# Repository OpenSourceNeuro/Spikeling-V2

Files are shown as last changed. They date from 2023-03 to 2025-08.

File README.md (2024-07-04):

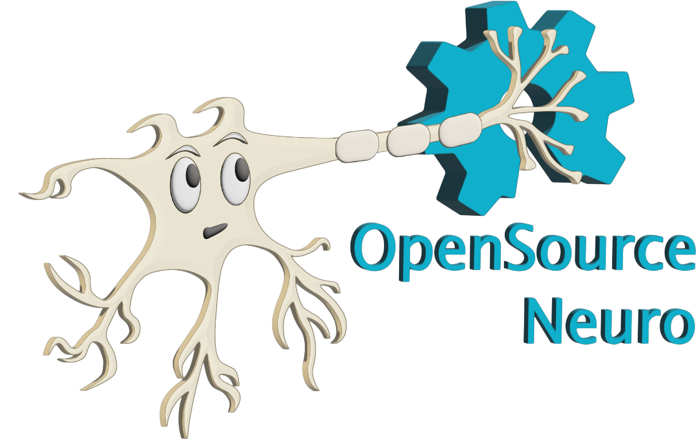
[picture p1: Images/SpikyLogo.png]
<p align="left">

<h1 align="center"> Spikeling V 2.2</h1></p>
<h3 align="center">  A hardware implementation of spiking neurons for neuroscience teaching and outreach</h3></p>
<p align="center"><h6 align="right">developed by M.J.Y. Zimmermann, A.M. Chagas & T. Baden</h6></p>

<br></br>



This project is licensed under the [GNU General Public License v3.0](https://github.com/OpenSourceNeuro/Spikeling-V2/blob/main/LICENSE)<br>
The hardware is licensed under the [CERN OHL v1.2](https://github.com/OpenSourceNeuro/Spikeling-V2/blob/main/PCB%20-%202.2c/LICENSE)

***

<p style='text-align: justify;'>
Understanding how neurons encode and compute information is fundamental to our study of the brain, but opportunities for hands-on experience with neurophysiological techniques on living neurons are scarce in science education.

<p style='text-align: justify;'>
Due to budgetary constraints and logistical hurdles, few students can be afforded the opportunity to experience electrophysiological recordings on living neurons in action. Yet, a fundamental aspect of neuroscience courses is to understand electrical signalling within neurons and the transmission of signals across synapses, as well as the experimental techniques necessary to observe these properties.

<p style='text-align: justify;'>
To support university-level neuroscience teaching, we designed ‘Spikeling’, an open-source teaching support device that mimics the electrical properties of spiking neurons by running the computationally efficient yet versatile Izhikevich model.

<p style='text-align: justify;'>
It is an artificial neuron that can receive different inputs, integrate them and outputs its computation, just like a spiking neuron would!

<p style='text-align: justify;'>
Technically, it consists on a microcontroller (an ESP32) running the computationally efficient Izhikevich model of a spiking neuron.

<br>

<div>
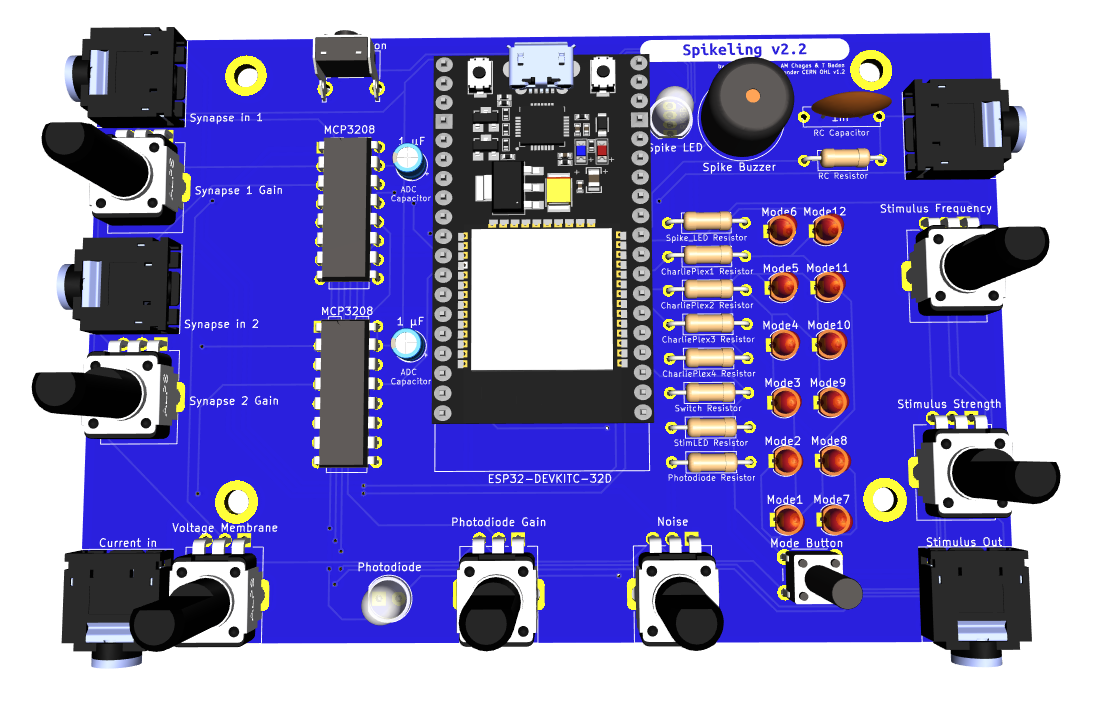
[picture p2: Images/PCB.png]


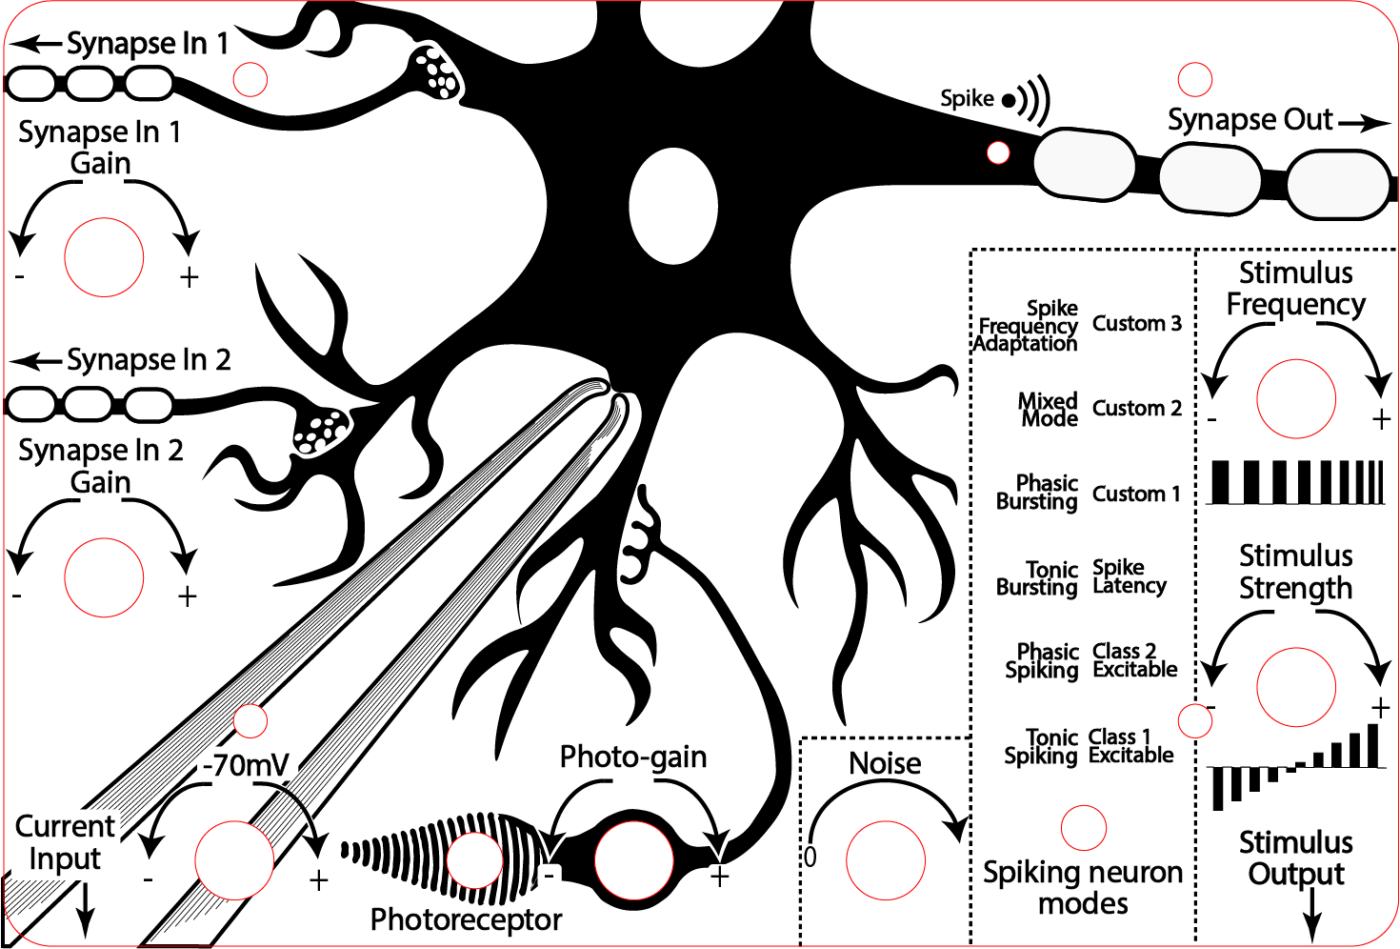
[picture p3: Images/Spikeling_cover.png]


<h6 align="center">Left: Rendering of spikeling electronic components. Right: Acrylic cover detailing spikeling functionalities.</h6>

</div>

<div>

<p style='text-align: justify;'>
The spikeling project emerged from local needs to teach neuroscience class modules for direct interaction with neuron physiology, data analysis, fluorescence imaging, protocol design, etc. The aim is to provide hands-on experience on how neurons encode information and how diverse variables modulates their activities, while engaging students with crucial aspects of data collection, experimental limitations, methodology and statistical analysis.

<p style='text-align: justify;'>
In order to give users a full interactive experience with the Spikeling neuron, a drawing engraved on the cover details in a neuro-morphic fashion all device functionalities. Furthermore, a spike-triggered LED and buzzer have been added to the device.

<p style='text-align: justify;'>
A dedicated GUI (Graphical User Interface) allows users to fully interact with Spikeling, plot all data generated and record them for further analysis.

<p style='text-align: justify;'>
Overall, Spikeling is a versatile device, allowing any teaching staff to conceive dry-lab tutorials or home assignments related to their own teaching course materials.

<p style='text-align: justify;'>
Enthusiasts and potential collaborators can source the electronic bits for this project from <a href="https://kitspace.org/boards/github.com/maxzimmer/spikeling-v2/">KitSpace</a></p>

</div>

***

<h2 align="center"> A brief summary of Spikeling functions</h3>

<br>

<div>

<h3 align="left"> Neurophysiology:</h3></p>

<p style='text-align: justify;'>
Spikeling is conceived on the Izhikevich model, which “reproduces spiking and bursting behaviour of known type of cortical neurons. The model combines the biologically plausibility of Hodgkin-Huxley-type dynamics and the computational efficiency of integrate-and-fire neurons” (E.M. Izhikevich, IEEE Transactions on Neural Networks, 2003, doi: 10.1109/TNN.2003.820440).

<p style='text-align: justify;'>
Students can appreciate playing with many variables that can be encountered in textbook or related to class material. A simulated patch-clamp experiment (represented by a pipette drawing on the top cover) allows students to “inject current” into the Spikeling neuron. They can furthermore modulate the amount of current injected, the speed and duration at which it is injected and observe the adaptation effect on a spiking neuron.

<p style='text-align: justify;'>
Spikeling also possesses a photodiode (modelized on the top cover as a photoreceptor) making Spikeling photo-sensitive. The photodiode mimics current inputs a photoreceptor would have on a spiking neuron. Students can appreciate the impact of a flash light onto the photoreceptor and investigate the different effects it may have. Ultimately, a supplied LED can be connected to the stimulus port and can then be controlled in frequency and intensity for controlled experiments. Advanced variable such as photoreceptor decay and recovery rate could also be investigated.

<p style='text-align: justify;'>
Each Spikeling unit possesses one “axonal” output and two “dendritic” inputs. Each dendritic input possesses a knob that can modulate the synaptic gain positively or negatively (mimicking excitatory and inhibitory synapses). In advanced stages, students could be encouraged to form neuronal networks. Auxiliary neurons can furthermore be stimulated synchronously from the “main neuron” experiment box to set a controlled environment.

</div>

<br>

<div>



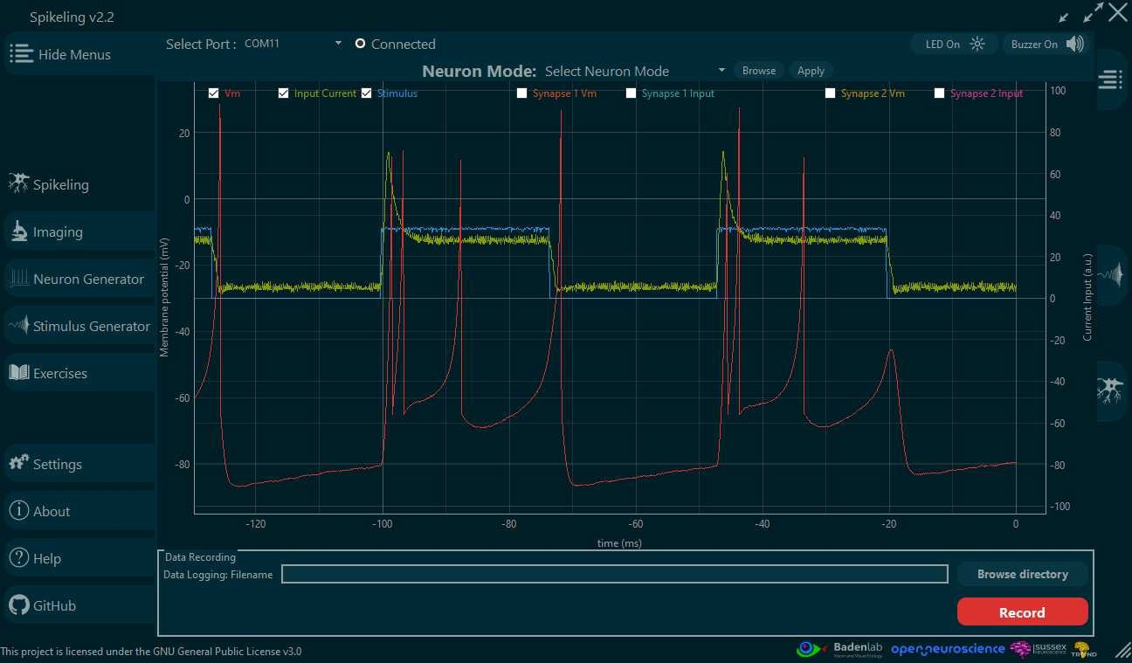
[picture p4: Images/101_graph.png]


<h6 align="center">Left: A Spikeling unit being stimulated by a direct current injection (blue cable) while receiving synaptic inputs from a second unit (pink cable). Right: Spikeling GUI displaying the unit membrane voltage (red trace) while being light-stimulated by a controlled LED (blue trace) which generates input current (green trace).</h6>

</div>

<br>

***

<br>

<div>

<h3 align="left"> Data analysis</h3></p>

<p style='text-align: justify;'>
Handling large dataset is an important part of daily academic work. However, few universities offer coding and programming modules for their neuroscience courses. A proper data analysis of any kind starts with the understanding of a program language and the understanding of every steps of the analysis pipeline. Only then, students can appreciate the results of their experiments and engage in their critical interpretation.

<p style='text-align: justify;'>
Any data generated by Spikeling can be saved and exported.  The GUI comes with a simple built-in data analysis that allows students to check their data and generate raster plots. From this simple analysis they could appreciate how neuronal information is encoded within stochastic spike trains (see below).

<p style='text-align: justify;'>
This simple analysis could be used for home assignments in the early stages of student degree before engaging them in developing their own analysis code.

<p style='text-align: justify;'>
For advanced data analysis and basic statistics, python notebooks are provided to serve as template for the teaching staff. It is our hope to create a Spikeling community where users could share courses, exercises and data analysis scripts to be widely used in neuroscience and coding courses.

</div>

<br>

<div>

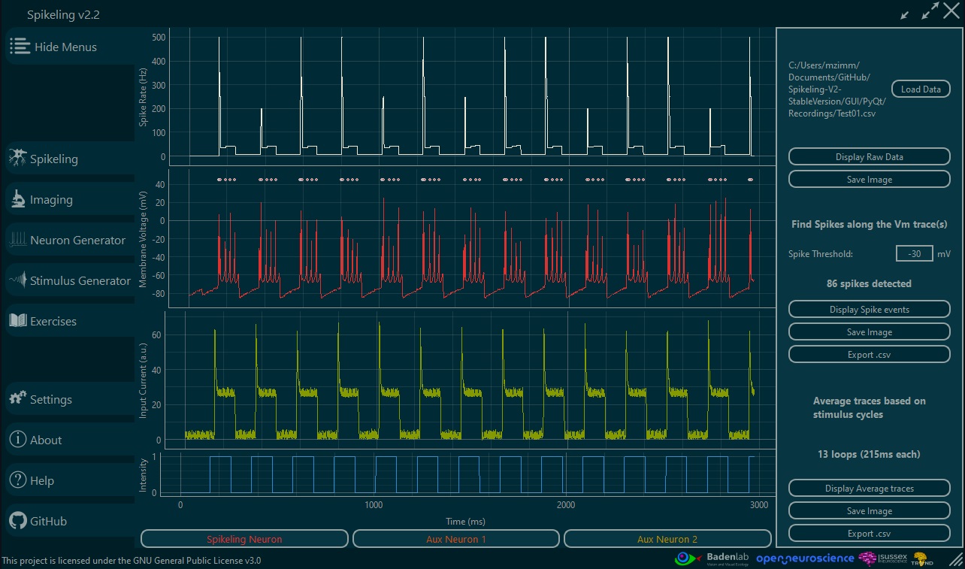
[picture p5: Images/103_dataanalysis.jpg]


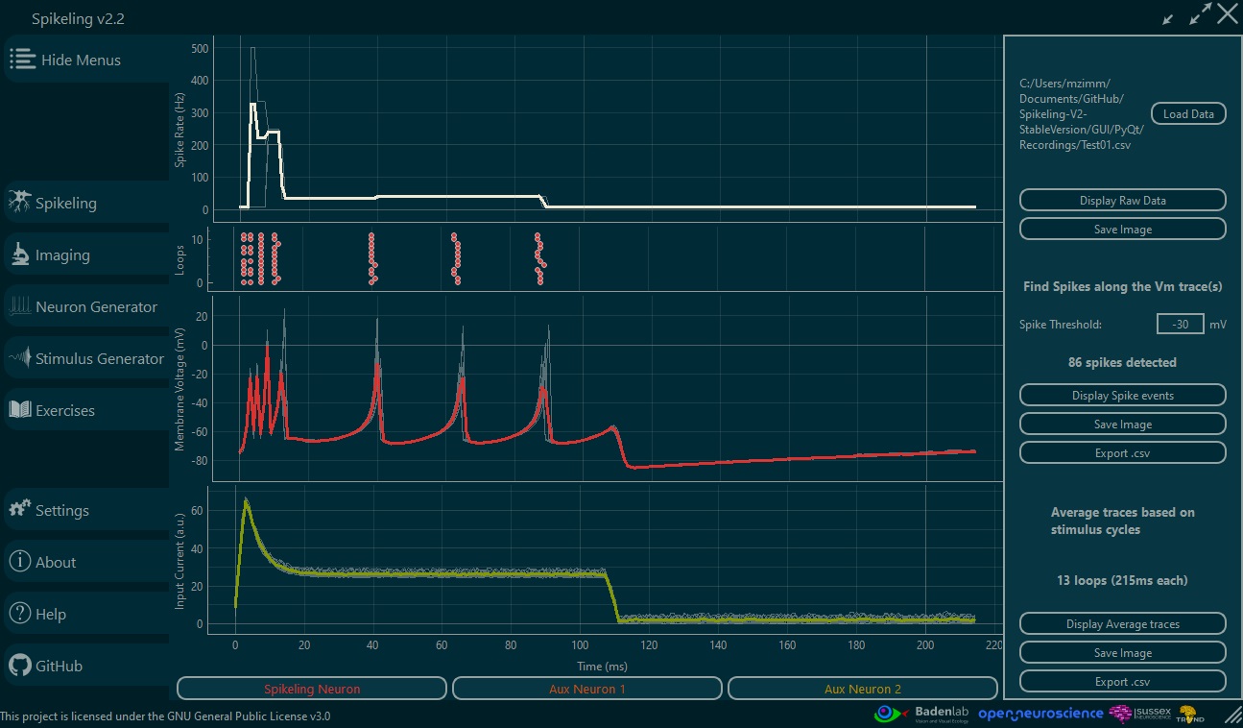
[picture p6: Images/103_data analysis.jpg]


<h6 align="center">GUI displaying the “Neuron Generator” page where users can appreciate the model underlying Spikeling activity and from which they can generate unique neuron to further run on Spikeling.</h6>

</div>

<br>

***

<br>

<div>

<h3 align="left">Stimulus generator:</h3>

<p style='text-align: justify;'>
Spikeling comes by default with a repeated square wave pattern stimulus, on which the user could only modulate the intensity and the frequency, might it be for direct current injection or light stimulation.

<p style='text-align: justify;'>
Here users are encouraged to develop their own stimulus (successive waves, sinusoidal loops, chirp, binary noise, etc.). Some basic stimuli are already available. The main point of this feature is to encourage the students to conceive their own experiments leading them to think about the protocol that needs to be implemented in order to answer the experimental questions they are being faced with.

</div>

<br>

<div>

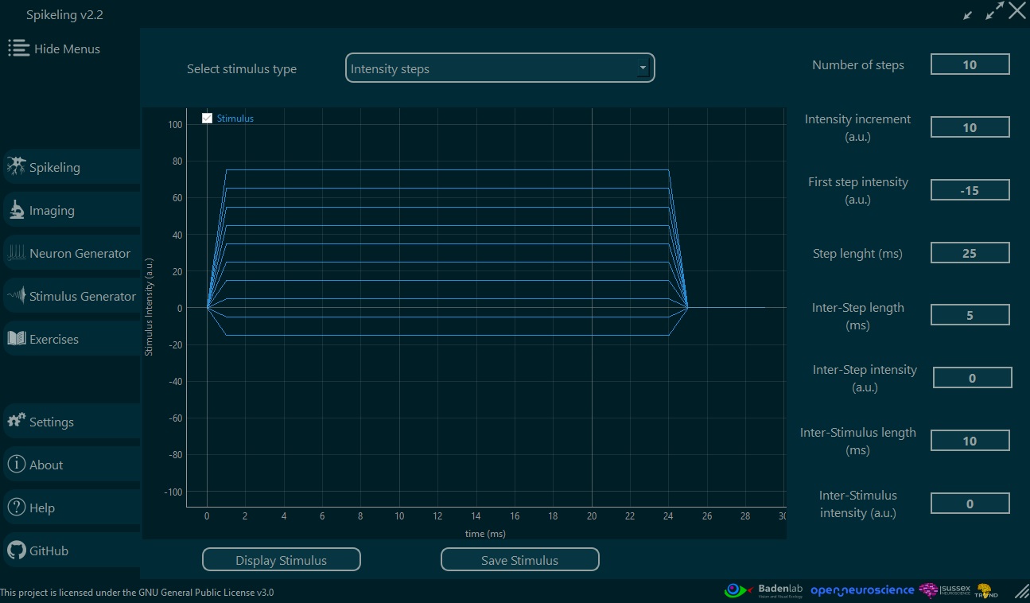
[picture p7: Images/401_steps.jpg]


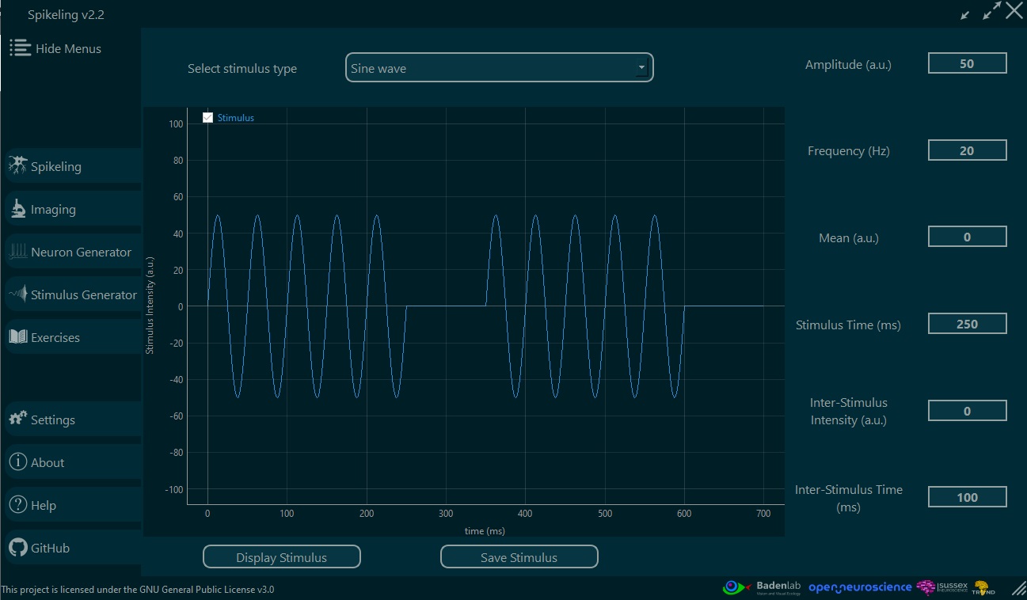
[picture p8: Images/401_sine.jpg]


<h6 align="center">GUI displaying the “Simulus Generator” page where users can generate their own unique stimuli. The left screen shows repetitive increments of current, as seen in classic electrophysiology experiments (10 steps with 10 a.u. current increment lasting 25 ms with a resting period of 5ms at 0 a.u. current). The right screen shows a sine wave stimulus (50 a.u. amplitude, 20 Hz frequency over a period of 250 ms and a resting period of 100 ms at 0 a.u. current)</h6>

</div>

<br>

***

<br>

<div>

<h3 align="left">Fluorescence imaging simulation:</h3>

<p style='text-align: justify;'>
Since Spikeling generates membrane voltage data, we could use this “ground truth data” to generate a simulated calcium concentration transient underlying spike occurrence in the neuron. And from then, use the later to model a simulated fluorescence.

<p style='text-align: justify;'>
Students could then be engaged into dynamic calcium fluorescence imaging (i.e two-photon microscopy) and play with many variables that could be encountered from the experimenter side (frame rate, laser power, photo detector gain, etc.), from the calcium concentration properties within the neuron (concentration baseline, decay, increase jump per spike, etc.)  or from the calcium indicator properties itself (indicator affinity, dissociation constant, brightness, photo-bleach, etc.).

<p style='text-align: justify;'>
For an even more realistic simulation, students could choose to move from a linear model to a non-linear saturation model of the fluorescence signal.

</div>

<br>

<div>

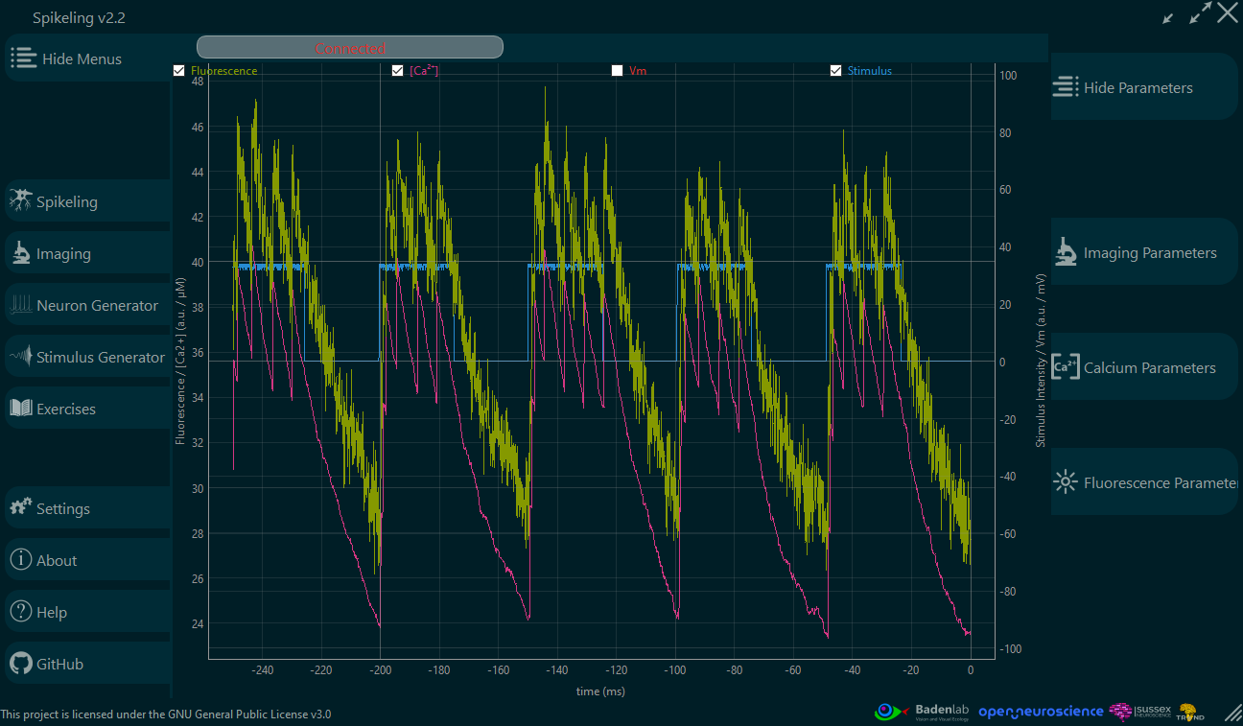
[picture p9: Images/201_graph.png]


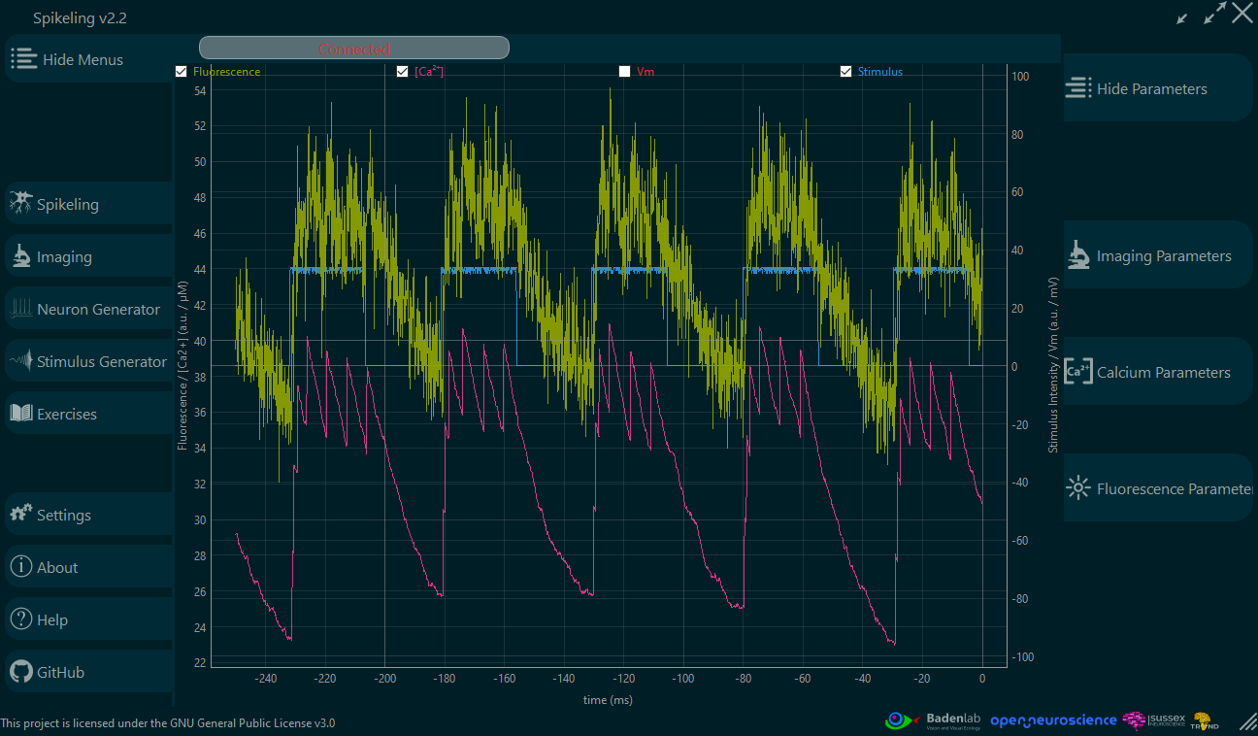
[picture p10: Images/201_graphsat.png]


<h6 align="center">GUI displaying linear(left) and (non-linear) models of simulated fluorescence (green) based on simulated calcium concentration (pink)</h6>

</div>

<div>

<p style='text-align: justify;'>
Here, the aim is to familiarise students with the type of data they could encounter in their future academic work, incorporating noise and limitations to the data that are inherent to every experiments.

<p style='text-align: justify;'>
Ultimately, students could be encouraged to analyse imaging data, even implement spike inference algorithms and compare their results to the “ground truth data” that generated the fluorescence trace.

</div>

<br>

***

<br>

<div>

<h3 align="left">Exercises:</h3>

<p style='text-align: justify;'>
Spikeling comes with a set of suggested exercises that could be used in class as a guideline for the teaching staff to explore Spikeling functionalities. They are conceived to allow students to make a concrete connection between neurophysiology concepts seen in lectures with a responsive in silico model.

<p style='text-align: justify;'>
Exercises are also a mean to introduce some epistemology into the teaching material: Understanding how a neurobiology concept became a knowledge and how it can be tested, confirmed or refuted.
In advance courses, giving students the opportunity to design their own experiment as assignment also allows to introduce good methodology and protocol design practices. Which, unfortunately has shown to be too often mistaken with methods.

<p style='text-align: justify;'>
We would always encourage teachers to develop their own exercises based on the content they cover in class. It is our hope that such exercises could also be used as homework grading system.

</div>

<br>

***

<br>

<h2 align="center">Detailed Spikeling functions</h3></p>

<br>

- [Spikeling: A spiking neuron interface](#a-spiking-neuron-interface)
- [Spikeling: GUI - neuron parameters](#spikeling-gui-neuron-parameters)
- [Spikeling: GUI - stimuli parameters](#spikeling-gui-stimuli-parameters)
- [Spikeling: Data Analysis](#-data-analysis)
- [Spikeling: Neuron generator](#spikeling-neuron-generator)
- [Spikeling: Stimulus Generator](#stimulus-generator)
- [Spikeling: Multiple recording](#spikeling-multiple-recording)

<br>

- [Fluorescence: imaging simulation](#fluorescence-imaging-simulation)
- [Fluorescence: Imaging parameters](#fluorescence-imaging-parameters)
- [Fluorescence: Calcium parameters](#fluorescence-calcium-parameters)
- [Fluorescence: Fluorescence parameters](#fluorescence-imaging-parameters)
- [Fluorescence: Data Analysis](#fluorescence-data-analysis)
- [Fluorescence: Multiple fluorescence](#fluorescence-multiple-fluorescence)

<br>

- [Exercices: GUI](#exercises-gui)
- [Exercices: Python](#exercises-python)

<br>

- [GitHub Contributions](#gitHub-Contributions)

- [Arduino code and libraries](#)

- [GUI PyQt6 / PySide6 script](#)

<br>

***

<br>

## A spiking neuron interface

<br>



<p style='text-align: justify;'>
The entire layout of the Spikeling board has been reconceived and a laser-cut acrylic sheet repesenting a neuron now sits on top of the board. All ports and potentiometers are now strategically placed.

<p style='text-align: justify;'>
The ESP32 is placed below the soma, the synaptic inputs from other Spikeling units are placed on the left, the synaptic output is placed on the right. Along the axon now sits a RGB LED, the red LED brightness follows as before the Vm status of the neuron, and the LED sparks in white when the neuron spike. The spike buzzer also sit along the axon, a small hole on the acrylic sheet sitting just above so the click can be heard coming from that direction. Both indicators can now be disabled by users at their pleasure.

<p style='text-align: justify;'>
The Vm potentiometer and the Current-in port are now grouped together and sit on the acrylic sheet at the bottom of an electrode pipette. They can now be considered as patch clamp experiment variables.

<p style='text-align: justify;'>
A photoreceptor is now drawn on the acrylic sheet, below the opsin sits a photodiode, and a potentiometer on the photoreceptor body now controls the photoreceptor sensitivity and its polarity (users can thus decide if the photoreceptor has an excitatory or an inhibitory effect on the neuron)

<p style='text-align: justify;'>
The noise potentiometer now sits in a box by itself as it represents parasitic noise from the experiment environment (synaptic inputs, receptor noise, thermal noise, experimental setup, etc.) and is independent from the rest of the Spikeling functions. This potentiometer is different from the others: it is not center-detented as it generates noise from a zero to a maximum value.

<p style='text-align: justify;'>
Next is the Neuron mode box which contains the twelve available modes to the users and a push button that allows the user to switch between them.

<p style='text-align: justify;'>
Finally, the last box contains all experimental tools allowing stimuli generation. As detailed on the acrylic top cover, the user can control the stimulus frequency and the stimulus intensity, along with its polarity. The stimulus output can either be directly connected to the current-in port to simulate a current applied to a patched neuron through the pipette; or be connected to a cable with a 5mm LED soldered at its tip which can be placed directly on top of the photoreceptor opsin (photodiode below). The photoreceptor potentiometer allows to modulate the gain and polarity of the light-induced input current. Furthermore, the photoreceptor possesses functions (on the GUI: decay/recovery) simulating how a variety of photoreceptors would integrate a light stimuli and how it will adapt to prolonged stimulation.  

<br>

***

<br>

<p style='text-align: justify;'>
Spikeling now possesses its own GUI, written in python and using the latest PyQt6/PySide6 library. The script then uses pyInstaller so it can be translated into a windows/linux/mac app, ready to be easily distributed to users.

<br>



<p style='text-align: justify;'>
The GUI is divided into distinct pages. The first one is the main GUI window where users connect the board to the computer. From there they can choose to either select the neuronal mode on the board directly (neuron mode box) or through the GUI (note that custom modes will have to be selected from here, and in this instance the GUI takes priority over the board commands).

<p style='text-align: justify;'>
The main window displays the Spikeling activity (Neuron Vm, total current input from all sources & stimulus ). If connected to other Spikelings, the GUI can display synaptic inputs: their incoming neuron Vm and their spiking events, which will be translated into input current for the main neuron. Traces can be selected through checkbox and superimposed over the same graph with a common timeline.

<p style='text-align: justify;'>
The "Neuron Mode" defines the current Izhikevich model being used [see Neuron Generator](#Spikeling-Neuron-generator). Twelve are encoded by default on the Spikeling unit and can be chosen either from the board itself or directly from the GUI: "Select Neuron Mode". Note that any command from the GUI will take priority over the board. Custom Neuron Modes can be selected from here and upload to the board.

<p style='text-align: justify;'>
The neuron interface page also possesses two buttons to enable/disable the spike buzzer sound and the spike LED, which in a class room full of spikeling, are regarded as huge relieves.

<p style='text-align: justify;'>
Below the main window, sits the recording window. All last generated data from traces that are checked on the main window will be saved in a .csv format.

<p style='text-align: justify;'>
On the right hand side two control columns can be found. For all commands, when the toggle button is enabled, the GUI takes over the potentiometer and controls directly the Spikeling variables. This allows users to design an experimental protocol in a controlled fashion.

<br>

***

<br>

<p style='text-align: justify;'>
Spikeling membrane voltage (Vm), displayed on the GUI in red, is generated by the Izhikevich model equation.
It is rather simple and relies on four parameters [see Neuron Generator](#Spikeling-Neuron-generator).

<br>

<p style='text-align: justify;'>
When Vm > 30mV, then a spike is generated, both the spike LED and spike buzzer on the board are activated, and the Vm model is reset accordingly (see above).

<p style='text-align: justify;'>
The green trace represents all current inputs received by the board and summed up in the variable "I" in the Izhikevich equation.
These current inputs correspond to the synaptic inputs, the direct current injection from the patch clamp port or the light induced current from the photodiode, and the noise generator potentiometer. All will influence the Vm equation and the subsequent spiking pattern.

<p style='text-align: justify;'>
The blue trace represents the square wave stimulus, which can be manually modulated in length, intensity and polarity through the potentiometer located in the "experiment box". The resulting stimulus signal is sent to the "Stimulus Output" port.
A jack cable connecting the "Stimulus Output" port to the "Current In" port will deliver the stimulus signal directly into the Spikeling neuron, simulating a direct current injection through a patched clamp electrode.
If a LED is connected to the "Stimulus Output" port and placed onto the photodiode, then the "photoreceptor" is stimulated accordingly and generates a current that will in turn be injected into the Izhikevich equation.

<p style='text-align: justify;'>
Users can also interact with the "Current In" potentiometer placed on the electrode and constantly inject steady current in order to either hyperpolarise or depolarise Spikeling.
Users can also interact with the "Photo-Gain" potentiometer and modulate the light sensitivity and polarity of the photodiode, thus generating ON/OFF neurons.

<p style='text-align: justify;'>
If Spikeling is connected to other units, the main window can display their Vm and their synaptic current inputs. Users can modulate these inputs by interacting with the "Synapse Gain" potentiometers which modulate the intensity and polarity of the synaptic inputs, giving rise to excitatory and inhibitory synapses.

<p style='text-align: justify;'>
Furthermore, users can stimulate the auxiliary Spikeling units in synchrony via the main unit's "Stimulus Output" port by using a splitter audio jack

<br>

***

<br>

## Spikeling GUI neuron parameters

<br>

TBC

<br>

***

<br>

## Spikeling GUI stimuli parameters

<br>

TBC

<br>

***

<br>

## Spikeling Neuron generator

<br>

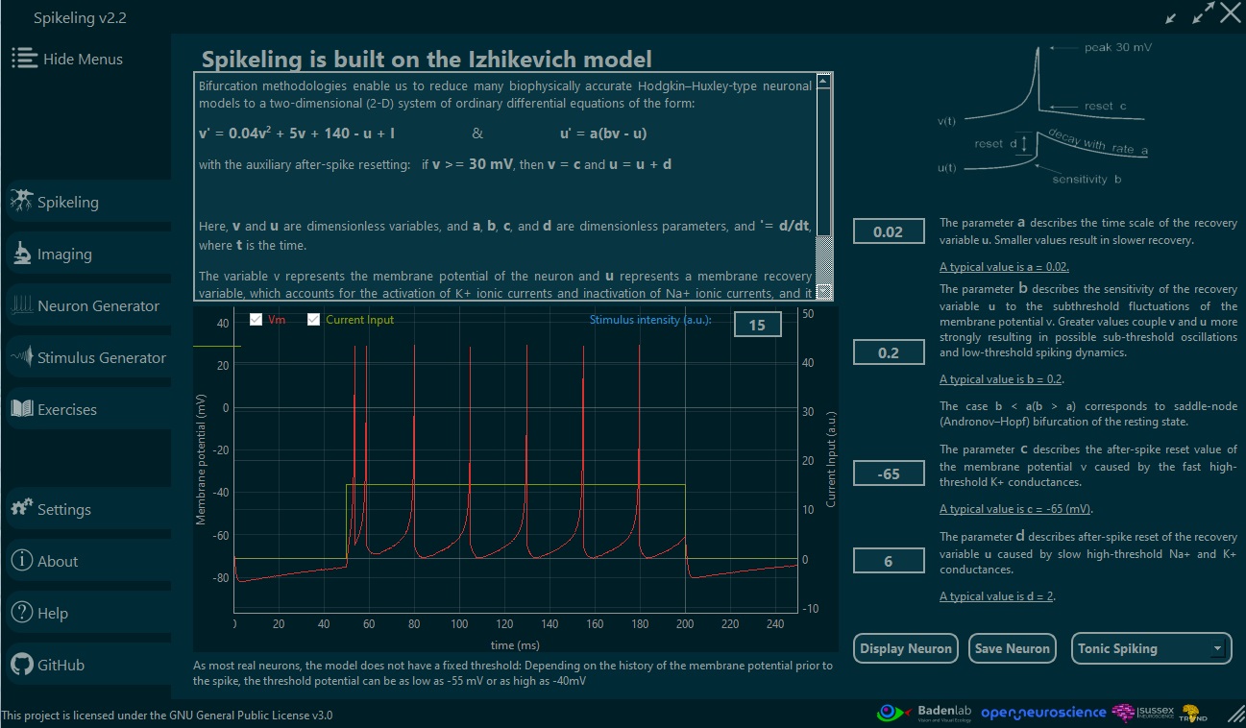
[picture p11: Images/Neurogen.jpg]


<p style='text-align: justify;'>
Spikeling GUI comes with a "Neuron Generator" page where users can interact with the Izhikevich equation, understand the model generating Spikeling membrane voltage, and create their own "neuron mode" to be loaded on the main page.

<p style='text-align: justify;'>
The main window computes the Izhikevich model with a modifiable current input. Users can change the 4 variable of the code and display the resulting "neuron mode". This is also where users can come up with their own neuronal modes to experiment on. This is also where teachers can generate their own custo-made neuron, save them, and impose them as experimental model for, i.e. home assignments.

<p style='text-align: justify;'>
From <a href="https://pubmed.ncbi.nlm.nih.gov/18244602">Izhikevich publication</a>:
<em> Bifurcation methodologies enable us to reduce many biophysically accurate Hodgkin–Huxley-type neuronal models to a two-dimensional (2-D) system of ordinary differential equations of the form:</em>

```math
v' = 0.04v^2 + 5v + 140 - u + I
```
```math
u' = a * (bv - u)
```

With the auxiliary after-spike resetting:

<p align="center">
if:
</p>

```math
v >= 30mV
```
<p align="center">
 then:
 </p>

 ```math
 v = c
 ```

<p align="center">
 and:
 </p>

 ```math
 u = u + d
```

<br>

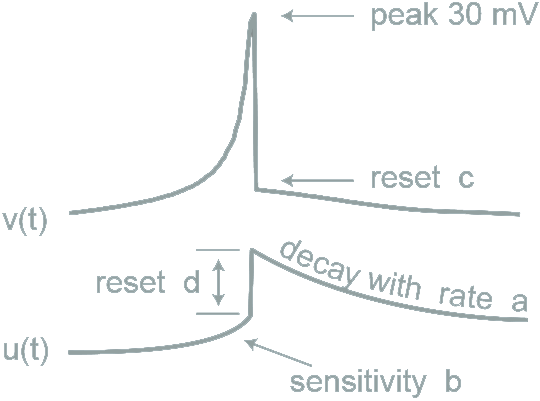
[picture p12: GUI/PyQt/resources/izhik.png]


<p style='text-align: justify;'>
Here, v and u are dimensionless variables, and a, b, c, and d are dimensionless parameters, and '= d/dt, where t is the time (0.1 µs).

<p style='text-align: justify;'>
The variable v represents the membrane potential of the neuron and u represents a membrane recovery variable, which accounts for the activation of K+ ionic currents and inactivation of Na+ ionic currents, and it provides negative feedback to v.

<p style='text-align: justify;'>
After the spike reaches its apex (+30 mV), the membrane voltage and the recovery variable are reset.
Synaptic currents or injected DC-currents are delivered via the variable I.

<p style='text-align: justify;'>
Below the stimulus frequency and strength sliders can be found a custom stimulus display. Here the user can choose to use instead of the classical square wave, either a stimulus from a pre-design library (comprising sine wave, chirp, white noise, etc.), or either a custom made stimulus generated from the GUI "stimulus generator" tab.

<br>

***

<br>

## Spikeling Stimulus Generator

<br>

<p style='text-align: justify;'>
Spikeling GUI also comes with a "Stimulus Generator" page where users can generate their own stimuli. In the current version seven distinct stimulus pattern are available with various parameters to interact with.
All stimuli can then be saved and further loaded from the Spikeling main window.

<br>

<div>





<h6 align="center">GUI displaying the “Simulus Generator” page where users can generate their own unique stimuli. The left screen shows repetitive increments of current, as seen in classic electrophysiology experiments (10 steps with 10 a.u. current increment lasting 25 ms with a resting period of 5ms at 0 a.u. current). The right screen shows a sine wave stimulus (50 a.u. amplitude, 20 Hz frequency over a period of 250 ms and a resting period of 100 ms at 0 a.u. current)</h6>

</div>

<br>

<div>

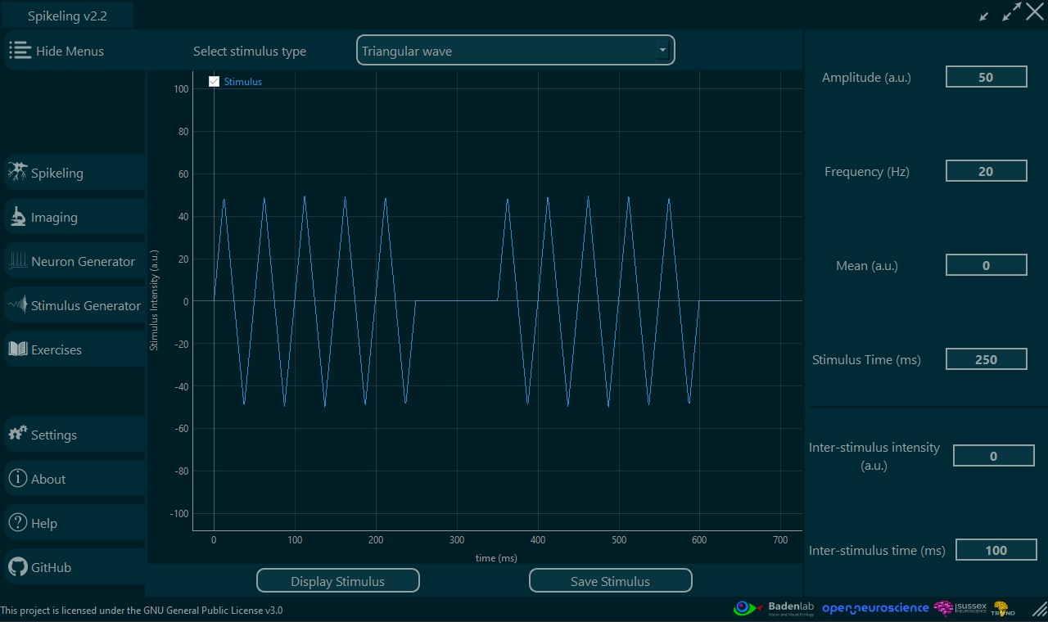
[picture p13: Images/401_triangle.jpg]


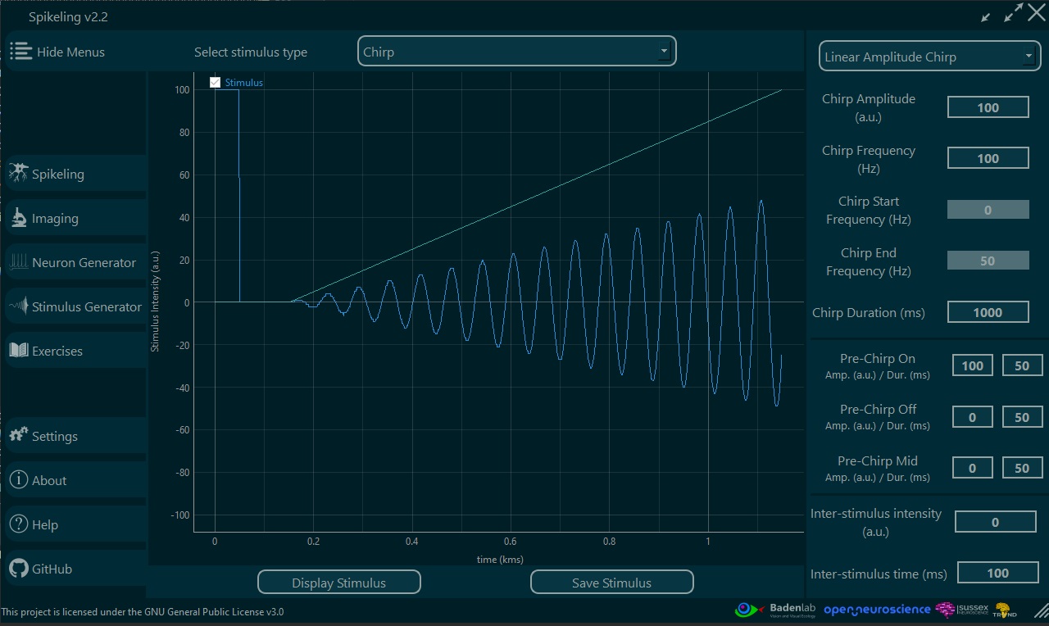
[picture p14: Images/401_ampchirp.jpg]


<h6 align="center">GUI displaying the “Simulus Generator” page where users can generate their own unique stimuli. The left screen shows a triangular wave stimulus (50 a.u. amplitude, 20 Hz frequency over a period of 250 ms and a resting period of 100 ms at 0 a.u. current). The right screen shows a chirp stimulus with an increased intensity from a 0 to a 100 a.u. amplitude at 100 Hz over 1000 ms </h6>

</div>

<br>

<div>

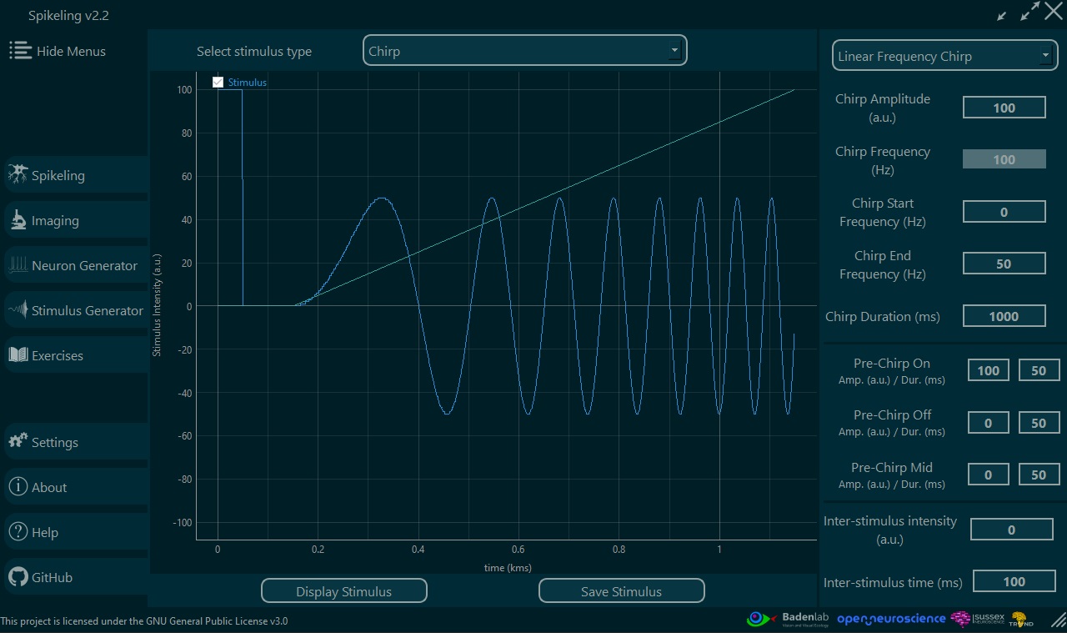
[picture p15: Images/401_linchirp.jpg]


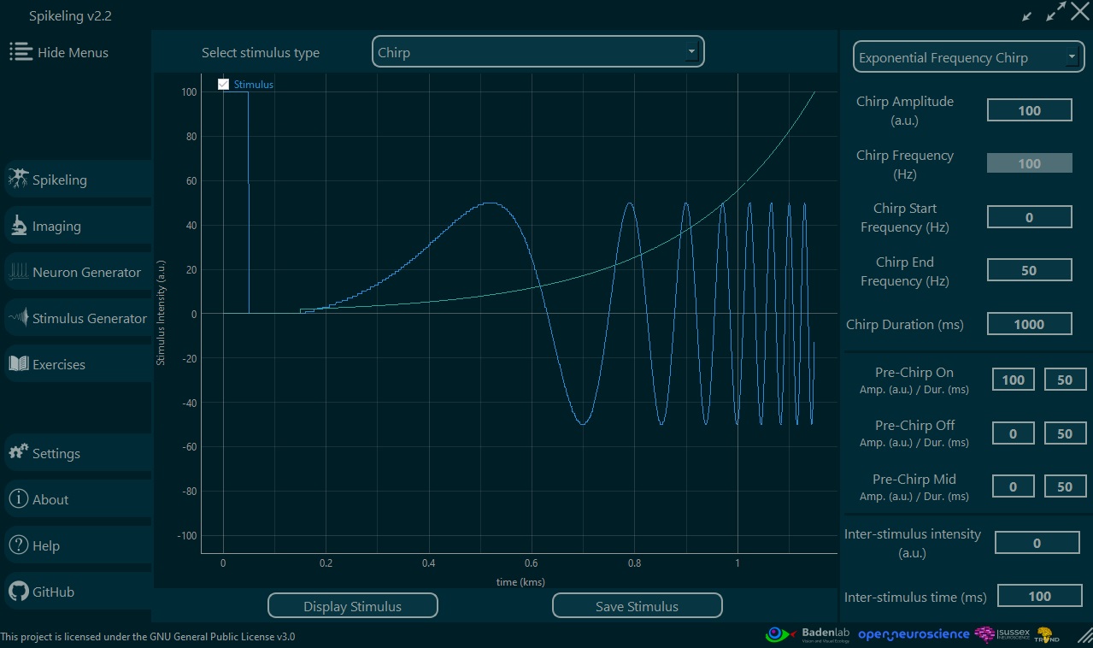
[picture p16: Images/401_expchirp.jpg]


<h6 align="center">GUI displaying the “Simulus Generator” page where users can generate their own unique stimuli. The left screen shows a linear chirp stimulus with an increased frequency from a 0 to a 50 Hz with an amplitude of 100 a.u. over 1000 ms. The right screen show the same stimulus with an exponential frequency increase </h6>

</div>

<br>

***

<br>

## Spikeling Multiple recording

<br>

TBC

<div>

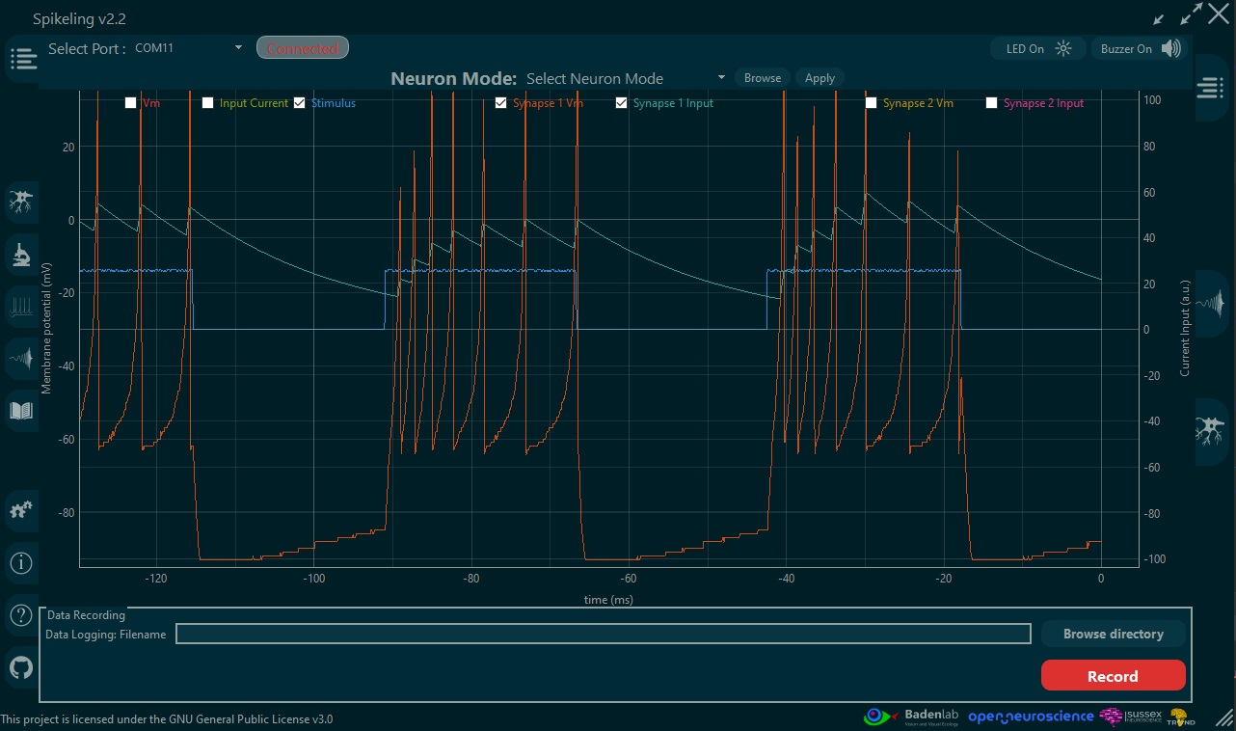
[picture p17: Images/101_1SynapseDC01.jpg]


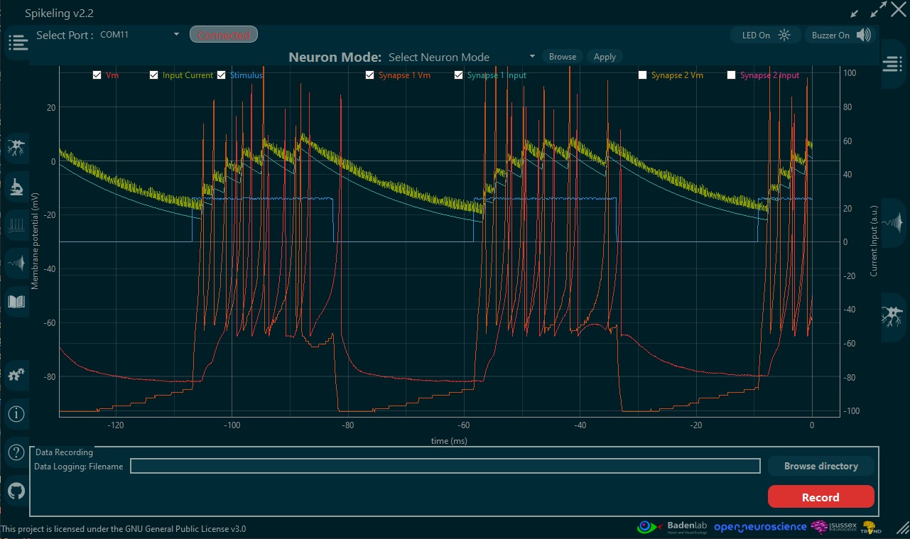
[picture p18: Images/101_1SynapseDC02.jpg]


<h6 align="center"> ... </h6>

</div>

<br>

<div>

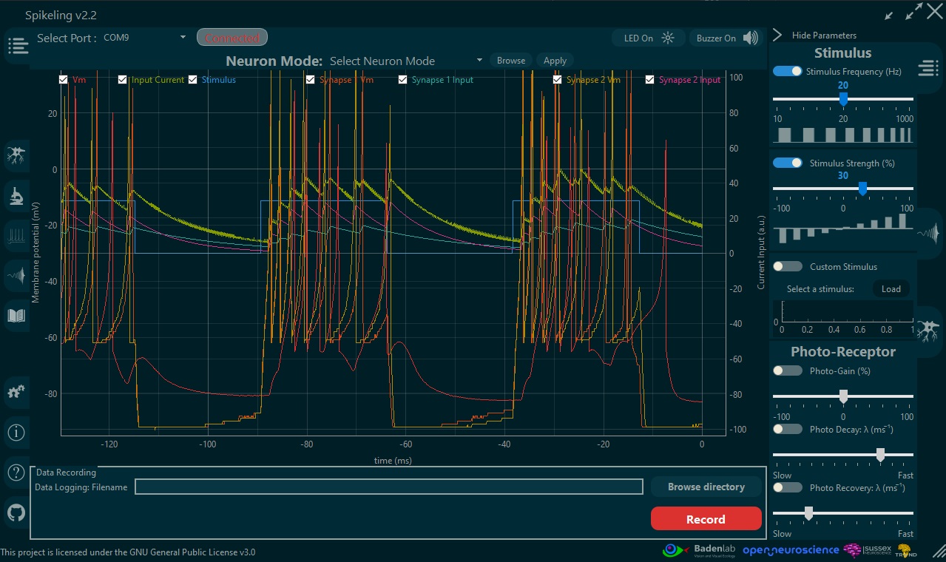
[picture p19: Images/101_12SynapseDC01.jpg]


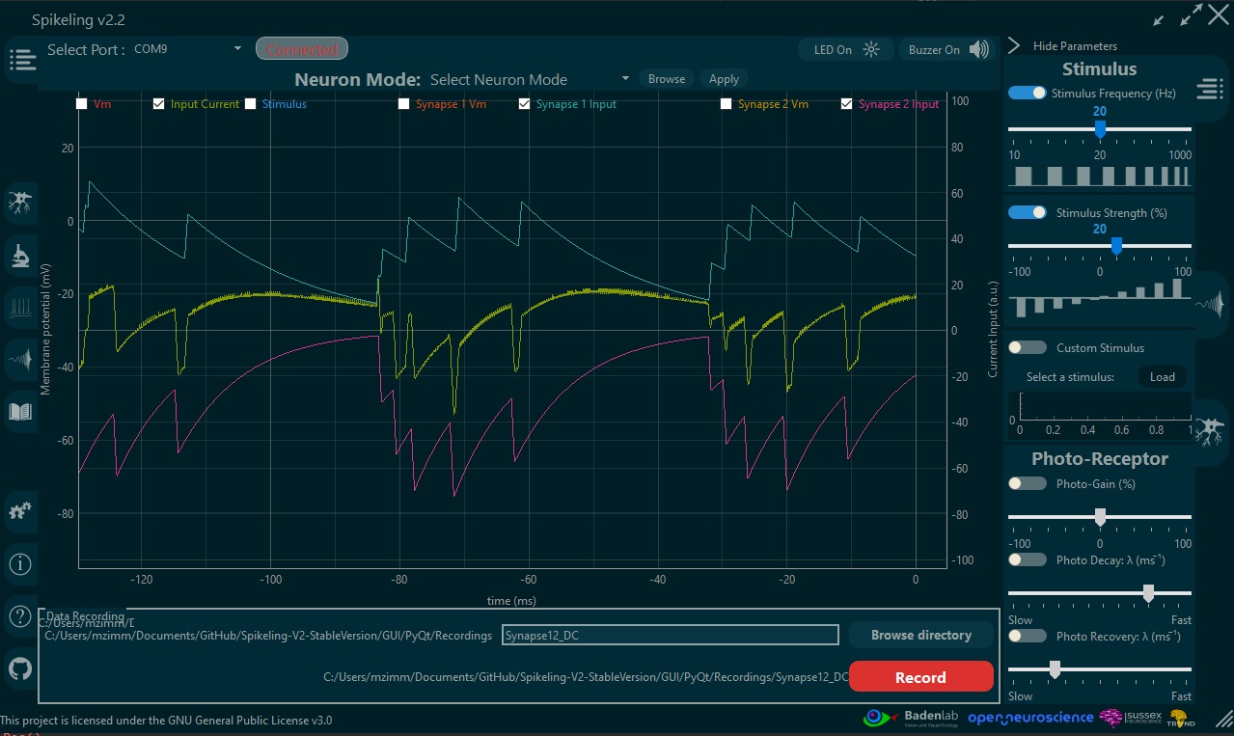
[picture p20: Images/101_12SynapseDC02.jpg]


<h6 align="center"> ... </h6>

</div>

<br>

***

<br>

## Fluorescence Imaging simulation

<br>

TBC

```math
[Ca^{2+}]_{t} = [Ca^{2+}]_{t-1} - \tau . [Ca^{2+}]_{t-1} + [Ca^{2+}]_{b} + A . n_{t} + \sigma_{Ca} . \sqrt{\Delta} . \varepsilon_{Ca,t}
```

Where:
- $\tau$ is the Calcium decay constant
- $[Ca^{2+}]_{b}$ the Calcium baseline concentration
- A is the calcium concentration jump each spike triggers
- $n_{t}$ is the number of spikes at time t
- $\sigma_{Ca}$ scales the Calcium noise
- $\Delta$ represents the imaging frame timeline
- $\varepsilon_{Ca,t}$ is a standard normal Gaussian noise source

<br>

```math
F_{t} = \alpha[Ca^{2+}]_{t} + \beta + \sigma_{F}.\varepsilon_{F,t}
```

<br>

<div>
<p align="center">


</div>

<br>

Where:
- $\alpha$ scales the Fluorescence
- $\beta$ offsets the fluorescence
- $\sigma_{F}$ scales the Fluorescence noise
- $\varepsilon_{F,t}$ is a standard normal Gaussian noise source

<br></br>

```math
Fsat_{t} = \alpha.S.[Ca^{2+}]_{t} + \beta + \eta_{t}

```

Where:
- The gain $\alpha$ scales the fluorescence. It accounts for all factors contributing to signal amplification, including the number of fluorophores in the neuron, the brightness of each fluorophore, the gain of the image acquisition system, etc.
- The offset $\beta$, accounts for any factor leading to a constant background signal, such as baseline fluorescence.
- $S . [Ca^{2+}]_{t}$ is a nonlinear saturation function, often taken as the Hill equation:
  - $S_{x} = \frac{x_{n}} {(x_{n} + kd)}$, where n is the Hill coefficient and kd the dissociation constant.
- Assuming the primary noise source is photon shot noise, it would be appropriate to model noise as a Poisson process, which could be well approximated by a Gaussian distribution for large photon counts: $\eta_{t}$

```math
\eta_{t} = \sqrt{\varepsilon.S . ([Ca^{2+}]_{t}) + \sigma_{F}} . \varepsilon_{F,t}
```

<br>

<div>

<p align="center">


</div>

<br>

***

<br>

## Fluorescence Imaging parameters

<br>

TBC

<br>

***

<br>

## Fluorescence Calcium parameters

<br>

TBC

<br>

***

<br>

## Fluorescence Imaging parameters

<br>

TBC

<br>

***

<br>

## Fluorescence Data Analysis

<br>

TBC

<br>

***

<br>

## Fluorescence Multiple fluorescence

<br>

TBC

<br>

***

<br>

## Exercises GUI

<br>

TBC

<br>

***

<br>

## Exercises Python

<br>

TBC

<br>

***

<br>

## GitHub Contributions

<br>

TBC

<br>

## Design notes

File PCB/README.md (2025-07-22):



<h1 align="center"> Spikeling v2 - Assembly Manual</h1></p>

<br></br>

## Overview

<p align="justify">
This page contains detailed assembly instructions for both version of La Spikeling unit, and includes a parts list for purchasing all electronics components.
Instructions on how to upload and update the microcontroller code and how to calibrate the device can be found <a href="https://github.com/OpenSourceNeuro/Spikeling-V2/tree/main/Instruction%20Manual"> <strong>on the instruction manual</strong> </a>.
Instructions regarding the GUI and on how to design stimuli can be found <a href="https://github.com/OpenSourceNeuro/LED-Zappelin-V2/blob/main/GUI_UserManual.md"><strong>here</strong></a>
</p>

***

- [Ordering PCB](#Ordering-the-PCB)
- [Assembling Spikeling](#Assembly)
- [Acrylic Covers](#Acrylic-Covers)

***

## Ordering the PCB

<p align="justify">
First step consist in getting the printed circuit board (PCB).
The PCB source files were designed on <a href="http://kicad.org/">KiCAD 9.0</a> and are available here to be modified by users if need be.
Users can find the "Gerber" files (zipped in the gerber folder) that companies (i.e. <a href="https://jlcpcb.com">JLCPCB</a>) will request to manufacture PCBs.
</p>

<p >


</p>

<br></br>

***
***

## Assembly

## Acrylic Covers

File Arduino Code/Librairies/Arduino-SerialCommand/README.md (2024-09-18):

# SerialCommand
A Wiring/Arduino library to tokenize and parse commands received over a serial port. 

additional usage for using custom serial object.

## Usage

* With default (Serial)
```Arduino
#include <SerialCommand.h>
SerialCommand parser;
```
* With Custom Serial
```Arduino
#include <SerialCommand.h>
SerialCommand parser(Serial2);
```
* With Custom Serial, and custom debug
```Arduino
#include <SerialCommand.h>
#define SERIALCOMMAND_DEBUG
SerialCommand parser(Serial2, Serial3);
```
* With Custom Serial and terminator
```Arduino
#include <SerialCommand.h>
SerialCommand parser(Serial2, '\r');
```

## PlatformIO

With PlatformIO those defines can be set in the `platformio.ini`:

```
build_flags =
	-DSERIALCOMMAND_DEBUG
	-DSERIALCOMMAND_BUFFER=64
	-DSERIALCOMMAND_MAXCOMMANDLENGTH=16
```

## History

This version advances the extended version by [Mingyu Kim](https://github.com/Mingyu-Kim/Arduino-SerialCommand).

The original version of this library was written by [Steven Cogswell](http://husks.wordpress.com) (published May 23, 2011 in his blog post ["A Minimal Arduino Library for Processing Serial Commands"](http://husks.wordpress.com/2011/05/23/a-minimal-arduino-library-for-processing-serial-commands/)).

This is a heavily modified version with smaller footprint and a cleaned up code by Stefan Rado.

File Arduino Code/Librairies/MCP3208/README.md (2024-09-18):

# MCP3208

Arduino Library for communication with the MCP3208 ADC 12-bit analog reader.
Based on the communication library for MCP3008 by Adafruit, manages 8 channels of simple analog reading or 4 channels of pseudo-differential reading.

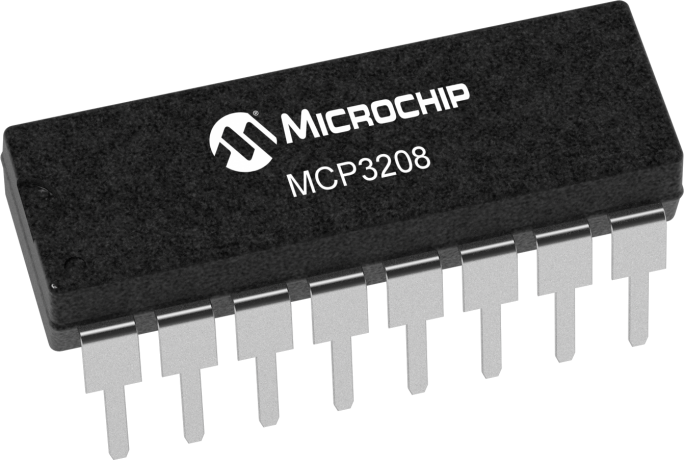
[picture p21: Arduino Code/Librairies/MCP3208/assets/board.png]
</a>

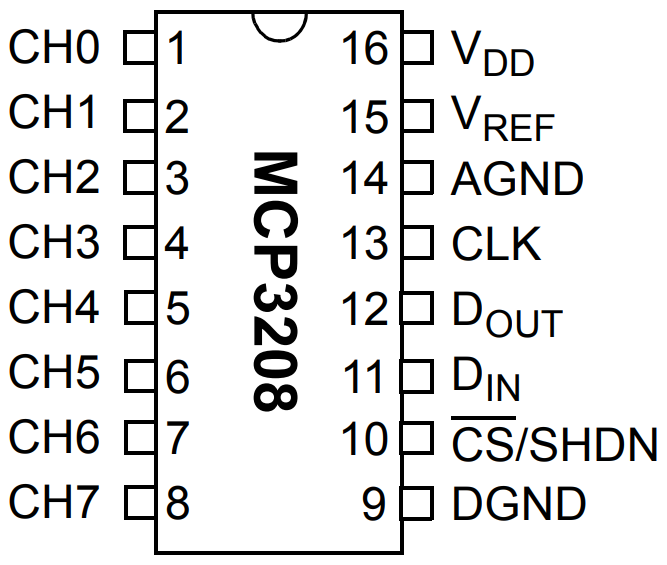
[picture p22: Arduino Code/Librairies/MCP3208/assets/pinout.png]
</a>

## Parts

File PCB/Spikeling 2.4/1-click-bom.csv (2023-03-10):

References | Qty | Description | Manufacturer | MPN | Manufacturer | MPN | Digikey | Mouser | RS | Newark | Farnell | LCSC | JLC Assembly
c1,c2 | 2 | 1µF electrolitic | Wurth Elektronik | 860160672002 |  |  | 732-9580-1-ND | 710860160672002 | 8399351
c3 | 1 | 1nF | KEMET | C901U102MYWDBA7317 | Vishay | A102K15X7RH5TAA | 1116PHCT-ND | 80C901U102MYWDBAP | 8773428 |  | 2440191
d1 | 1 | photodiode 5mm | Osram Opto | SFH 203 |  |  | 475-2649-ND | 720SFH203 | 247240
d2,d3,d4,d5,d6,d7,d8,d9,d10,d11,d12,13 | 11 | led 3mm | Kingbright | L-34QBC-D | Dialight | 521-9901-802F | 350-2318-ND | 6455219901802F | 8622872
d14 | 1 | rgb led 5mm | Kingbright | L-154A4SURKQBDZGW |  |  | 350-5218559F-ND | 6455218559F | 8614307
j1,j2,j3,j4,j5 | 5 | audio jack 90 degree 3 pin | RS Pro | 9131009 |  |  |  |  | 9131009
R1 | 1 | 10ohm | TE Connectivity | LR1F10R |  |  | A105948CT-ND | 279LR1F10R | 1251154
r3,r4,r6,r7,r8,r9 | 6 | 100ohm | TE Connectivity | LR1F100R |  |  | A105946CT-ND | 279LR1F100R | 1251155
r2,r5 | 2 | 10kohm | TE Connectivity | CFR25J10K |  |  | A105985CT-ND | 279CFR25J10K | 131378
rv1,rv2,rv3,rv4,rv5,rv6,rv7 | 7 | detented potentiometer | Bourns | PTV09A-4225F-B103 |  |  | PTV09A-4225F-B103-ND | 652PTV09A4225FB103 | 8274990
sw1 | 1 | mode switch | TE Connectivity | 3-1825910-1 |  |  | 450-1643-ND | 506FSM16JH | 4791463
sw2 | 1 | reset button switch | Omron | B3F-3120 |  |  | SW407-ND | 653B3F3120 | 6866884
u1 | 1 | esp32
u2,u3 | 1 | MCP3208-B | Microchip | MCP3208-BI/P |  |  |  | 579MCP3208BI/P | 3792487 |  | 1863934
 | 2 | support for mcp3208 chips | ASSMANN WSW Components | A 16-LC-TT |  |  | AE9992-ND |  | 6742432
 | 1 |  | Bourns

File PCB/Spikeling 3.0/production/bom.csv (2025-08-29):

Designator | Footprint | Quantity | Value | LCSC Part Number
B1 | BUZ-TH_L12.0-W12.0 | 1 | 4kHz | C7421651
C1, C3 | C_1206 | 2 | 22uF | C5672
C10 | C_0402 | 1 | 3.3pF | C1565
C11 | C_0603 | 1 | 1nF | C1588
C12, C4, C5, C6, C7, C8, C9 | C_0402 | 7 | 100nF | C1525
C2 | C_0603 | 1 | 10uF | C19702
D1 | SOD-323_L1.8-W1.3-LS2.5-RD | 1 | 1N5817WS | C489146
D2, D3, D4 | SOD-523_L1.2-W0.8-LS1.6-BI | 3 | LESD5D5.0CT1G | C383211
D5 | D_0603 | 1 | Red | C2286
D6 | SENSOR-TH_BPW34S-Z | 1 | BPW34S-Z | C67891
D7 | LED-SMD_4P-L3.2-W2.8-BL | 1 | MHPC3528CRGBCT | C2962096
J1 | TYPE-C-SMD_HX-TYPE-C-16PIN | 1 | Connector, USB-TYPE-C-16P | C2927039
J2, J3, J4, J5, J6 | AUDIO-SMD_PJ-320B | 5 | PJ-320B贴片 | C18594
L1 | L0805 | 1 | BLM21PG221SN1D | C85840
R1, R2, R3 | R_0603 | 3 | 5.1kΩ | C23186
R10, R5, R8 | R_0603 | 3 | 100Ω | C22775
R11, R12, R4 | R_0603 | 3 | 10kΩ | C25804
R6 | R_0603 | 1 | 0Ω | C21189
R7 | R_0603 | 1 | 1MΩ | C22935
R9 | R_0603 | 1 | 10Ω | C22859
SW1 | SW_TS-1088-AR02016 | 1 | Tactile Button, 160gf | C720477
SW2, SW3, SW4 | KEY-TH_4P-L7.5-W6.8-P4.50-LS7.2 | 3 | SKHHLVA010 | C110289
U1 | ESP32-S3-WROOM-1 | 1 | ESP32-S3-WROOM-1 | C2913197
U2 | SOT-223-3_L6.5-W3.4-P2.30-LS7.0-BR | 1 | AMS1117 | C6186
U3, U4 | SOIC-16_L9.9-W3.9-P1.27-LS6.0-BL | 2 | MCP3208T-CI/SL | C626764
U5 | VSSOP-8_L3.0-W3.0-P0.65-LS4.9-BL | 1 | OPA380AIDGKR | C2057355
VR1, VR2, VR4, VR5, VR6, VR7 | RES-TH_RK09D1130C3C | 6 | 10kΩ | C470316
VR3 | RES-TH_RK09D1130C2P | 1 | 10kΩ | C361173

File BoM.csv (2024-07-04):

Name | Manufacturer | Manufacturer ID | Retailer | Retailer ID | Quantity | Observation 1 | Suggested URL | Cost
ESP32 Dev module | Espressif Systems | ESP32-DEVKITC-VE | Digikey | 1965-ESP32-DEVKITC-VE-ND | 1 |  | https://www.digikey.co.uk/en/products/detail/espressif-systems/ESP32-DEVKITC-VE/12091812
Detent potentiometer | Bourns | PTV09A-4225F-B103 | RS | 827-4990 | 6 | Syn1, Syn2, Vm, PD, Fr, St | https://uk.rs-online.com/web/p/potentiometers/8274990?searchId=22493bc3-c651-455c-9294-958e63f149a7&gb=s
No-detent potentiometer | Bourns | PTV09A-4025F-B103 | RS | 181-4488 | 1 | Noise | https://uk.rs-online.com/web/p/potentiometers/1814488?searchId=5138736d-87d0-4a75-9752-bf8f8f23c40a&gb=s
3.5mm jack connector | RS-Pro | 913-1009 | RS | 913-1009 | 5 |  | https://uk.rs-online.com/web/p/jack-plugs-sockets/9131009?searchId=2c0336f3-d739-40b2-949a-42ff9f557dda&gb=s
Plunger Tactile Switch | Omron | B3F-3120 | RS | 686-6884 | 2 |  | https://uk.rs-online.com/web/p/tactile-switches/6866884?searchId=70f29464-77be-4218-9553-7f822bebb458&gb=s
Tactile Switch | Alps Alpine | SKHHDHA010 | RS | 758-1975 | 1 |  | https://uk.rs-online.com/web/p/tactile-switches/7581975?gb=s
Piezo Buzzer | RS-Pro | 181-2739 | RS | 181-2739 | 1 |  | https://uk.rs-online.com/web/p/piezo-buzzers/1812739?searchId=69850575-7d3e-4b5f-a63a-7f8974e75ec1&gb=s
Photodiode | ams OSRAM | SFH 203 P | RS | 654-8671 | 1 |  | https://uk.rs-online.com/web/p/photodiodes/6548671?searchId=9db1ab38-9fea-4dfe-ad95-fc149c7bcfdf&gb=s
10? Resistor | RS-Pro | 707-7509 | RS | 707-7509 | 1 |  | https://uk.rs-online.com/web/p/through-hole-resistors/7077509?searchId=0bd241c4-7fd2-4b35-94cd-a7251b73cba4&gb=s
10k? Resistor | RS-Pro | 707-7745 | RS | 707-7745 | 3 |  | https://uk.rs-online.com/web/p/through-hole-resistors/7077745?searchId=7aa2fa83-7976-4765-98da-bd94c03fa660&gb=s
220? Resistor | RS-Pro | 707-7612 | RS | 707-7612 | 5 | Replace the 100?, depending on the top acrylic opacity, adjusting these resistor values modify LEDs brightness
DIP 16 | ASSMANN WSW | A 16-LC-TT | RS | 674-2432 | 2 |  | https://uk.rs-online.com/web/p/dil-sockets/6742432?searchId=86e0a296-b2f8-4870-8640-661f18704577&gb=s
MCP3208 | Microchip | MCP3208-CI/P | RS | 379-2516 | 2 |  | https://uk.rs-online.com/web/p/analogue-to-digital-converters/3792516?searchId=1d16ee8c-3275-450b-b003-6397808660eb&gb=s
1?F Capacitor | RS-Pro | 711-2103 | RS | 711-2103 | 2 |  | https://uk.rs-online.com/web/p/aluminium-capacitors/7112103?searchId=3bd5c97d-0696-4fca-8943-63c37c72144c&gb=s
1nF Capacitor | Vishay | HVCC153Y6P102KEAX | RS | 204-2380 | 1 |  | https://uk.rs-online.com/web/p/single-layer-ceramic-capacitors/2042380?gb=s
Potentiometer knob | Sifam | 3/03/DR110-006/237/233 | RS | 299-4907 | 7 |  | https://uk.rs-online.com/web/p/potentiometer-knobs/2994907?searchId=1bc9294d-ccd6-49b0-b7ef-d202f5742ca7&gb=s
3mm LED | Kingbright | L-34QBC-D | RS | 862-2872 | 12 | Select any colour relevant or matching the top acrylic
Common Cathode RGB LED | Kingbright | L-154A4SURKQBDZGW | RS | 861-4307 | 1 |  | https://uk.rs-online.com/web/p/leds/8614307?gb=s
M3 x M3 Thread, 5mm Body | RS-Pro | 606-670 | RS | 606-670 | 4 |  | https://uk.rs-online.com/web/p/standoffs/0606670?searchId=bd61539a-c524-4924-a727-4a801f65e7a6&gb=s
M3 x M3 Thread, 10mm Body | RS-Pro | 222-395 | RS | 222-395 | 4 |  | https://uk.rs-online.com/web/p/standoffs/0222395?searchId=7eb9d18b-541a-4336-a950-aaf816f4ba9f&gb=s
Screws DIN 7985, M3x6mm | RS-Pro | 190-428 | RS | 190-428 | 8 |  | https://uk.rs-online.com/web/p/machine-screws/0190428?searchId=1c54ddf7-234e-442e-84dc-f56f64f62ed1&gb=s

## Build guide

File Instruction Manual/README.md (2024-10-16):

<p align="left">

<h1 align="center"> Instruction Manual</h1></p>

<h2 align="left"> Overview</h1></p>

<p style='text-align: justify;'>

This document contains detailed instructions to connect, install and use Spikeling v2.2

The hardware itself is controlled by a <a href="https://www.espressif.com/en/products/devkits/esp32-devkitc">ESP-32 development board</a> (ESP-32 WROVER-E). It runs on a C++ code which can be updated through the <a href="https://www.arduino.cc">Arduino IDE</a>. The <a href="https://github.com/OpenSourceNeuro/Spikeling-V2/tree/main/Arduino%20Code">Arduino Code session</a> in this repository details how to modify the Spikeling code.

<strong>In order to communicate with the ESP-32 micro-controller, users must first install the latest SiLabs <a href="https://www.silabs.com/developers/usb-to-uart-bridge-vcp-drivers">CP210x driver</a></strong>

The software itself consists on a Graphical User Interface (GUI) built on python using the pyqt6/pyside6 library packages:
  - Users can run the <a href="https://github.com/OpenSourceNeuro/Spikeling-V2/tree/main/GUI/PyQt">python code</a> directly by executing the <strong>Main.py</strong> file.
  - A Windows executable file is also available and can be found <a href="https://github.com/OpenSourceNeuro/Spikeling-V2/blob/main/GUI/Windows/Spikeling.exe">here</a>
  - A Linux version is available <a href="">here</a>
  - And a Mac version <a href="">here</a>

  </p>

  ***

  ## Driver Installation

  <br>

  Spikeling runs on an Espressif ESP32 board and requires the USB to UART bridge <a href="https://www.silabs.com/developers/usb-to-uart-bridge-vcp-drivers"> CP210x driver</a>,  which can be downloaded<a href="https://www.silabs.com/developers/usb-to-uart-bridge-vcp-drivers?tab=downloads"> <strong>here</strong></a>.

  Once the driver has been installed, users can operated the GUI (c.f. <a href="https://github.com/OpenSourceNeuro/Spikeling-V2/tree/main/GUI"> GUI UserManual</a>) or modify the <a href="https://github.com/OpenSourceNeuro/Spikeling-V2/tree/main/Arduino%20Code/Spikeling_V2_2">microcontroller code</a> through the Arduino Integrated Development Environment (IDE).

  <br></br>

  ## Microcontroller Arduino code

  <br>

  ##### Arduino IDE

  <br>

  The ESP32 microcontroller runs a C++ code which can be accessed via the Arduino IDE, which can be downloaded <a href="https://www.arduino.cc/en/software">here</a>.

  <br>

  ##### ESP32 Add-on

  <br>

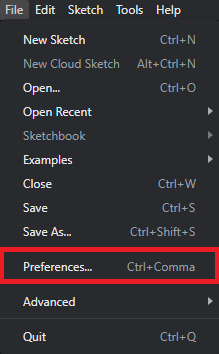
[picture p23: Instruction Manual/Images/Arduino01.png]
  

  Once the IDE is installed, users needs to install the ESP32 board library:

  In the Arduino IDE, go to <strong> File > Preferences </strong>

  Enter the following link into the <strong>Additional Board Manager URLs</strong> field:

  https://raw.githubusercontent.com/espressif/arduino-esp32/gh-pages/package_esp32_index.json

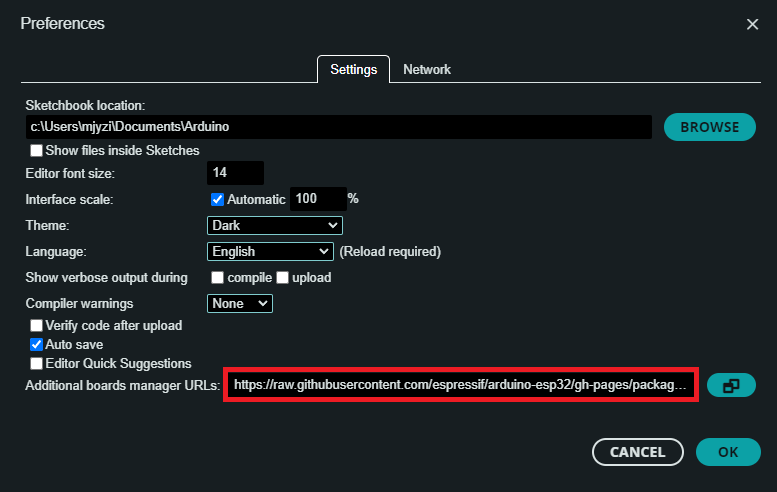
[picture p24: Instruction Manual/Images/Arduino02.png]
  
  Then click on the <strong>OK</strong> button.

  <br></br>

  Next, open the Boards Manager. Go to <strong> Tools > Board > Board Manager...</strong>

  Search for ESP32 and press install button for the <strong>ESP32 by Espressif Systems</strong>.

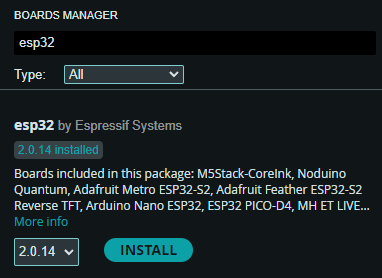
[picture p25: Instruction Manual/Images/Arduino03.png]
  
  Then click on the <strong>Install</strong> button.

  <br></br>

  ##### Compiling the code

  <br>

  Within the Arduino IDE, user needs to select the FQBN (Fully Qualified Board Name) on which the code will be compiled for.

  Here the ESP32 Dev Module needs to be selected.

  Go to <strong>Tools > Board > esp32 > ESP32 Dev Module </strong>

  
  The board name should be displayed  as shown.

  <br></br>

 ##### Installing Libraries

  <br>

  Before compiling the Spikeling code, a few libraries need to be installed:
    - Arduino-SerialCommand
    - MCP3208 by Rodolfo Pietro
    - Gaussian by Ivan Seidel

  Most of them can be downloaded from the Arduino IDE: Go to <strong>Sketch > Include Library > Manage Libraries</strong>, enter the library name, then install it following the same process as for the board library.

  We however recommend for the Arduino-SerialCommand library to manually place the library folder which can be found <a href="https://github.com/OpenSourceNeuro/Spikeling-V2/tree/main/Arduino%20Code/Librairies">here</a> into the library folder. For Windows Users: <strong>C:/Users/x/Documents/Arduino/libraries</strong>

  Now everything is set to compile and verify the code.

  Users can now select the COM port on which the ESP32 is connected ( Go to <strong>Tools > port</strong> ) and upload the code onto the board.

  <br></br>
  ***

<h2 align="left">Spikeling GUI</h2></p>

Once the CP210x has been installed, users can launch the Spikeling software.

On the home page, menus can be found on the left tab

<br></br>


<h4 align="left"> Spikeling Menu</h4>

<br></br>

<p style='text-align: justify;'>
In the Spikeling tab, users need to select <strong> Neuron Interface </strong> in order to display the main oscilloscope screen on which all traces will be displayed

<p style='text-align: justify;'>
To connect the Spikeling device with the GUI, <strong>select a COM port</strong>. If several are available, the correct COM port should make the device's LEDs light up in sequence. Then click <strong> Connected</strong>

<p style='text-align: justify;'>
From now on, the oscilloscope should display three traces. by default, the Spikeling Vm, the total input current it is receiving, and the stimulus output. Traces can be selected or unselected from the oscilloscope, to only the ones of interest.

<br></br>

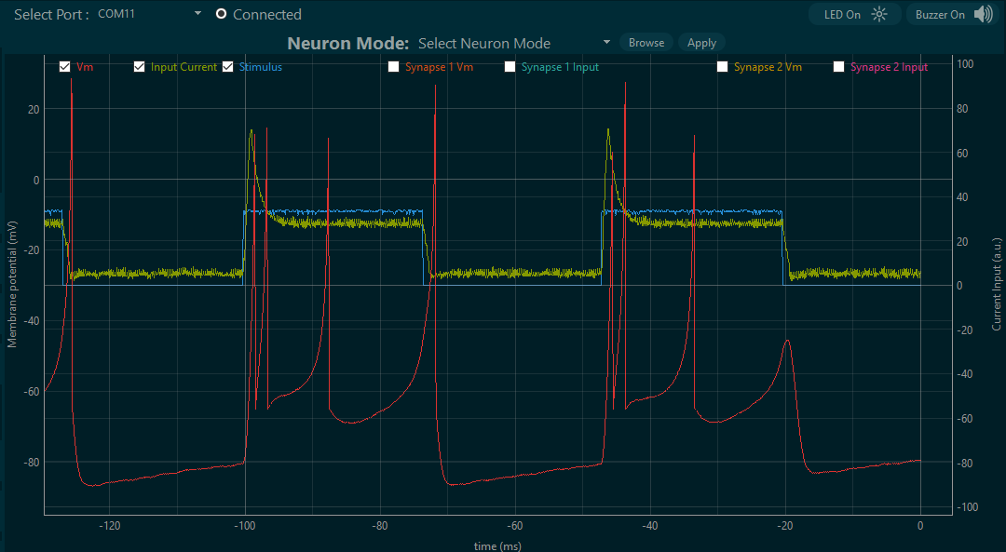
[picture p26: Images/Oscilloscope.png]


<p style='text-align: justify;'>
The first three traces concern the Spikeling device to which the computer is connected. the next two concern a second Spikeling unit connected to the main one through the <strong> Synapse in 1</strong> plug. The last two concern a third unit connected to the <strong> Synapse in 2</strong> plug.

<p style='text-align: justify;'>
On the top right corner, two buttons can be found <strong> LED On</strong> and <strong> Buzzer On</strong>, which can respectively silence the device LED and buzzer.

<p style='text-align: justify;'>
Neuron modes can be manually selected on the board by pushing the button on the bottom right corner of the spikeling device. Or it could be directly selected from the software by selecting one of the twelve default modes. Note that for this neuron mode change to be efficient, one need to click on the <strong> Apply</strong> button.

<p style='text-align: justify;'>
Furthermore, unique neuronal modes can be generated by the users on the <strong>Neuron Generator</strong> tab (see below). Such neuron modes can be selected by clicking in the <strong>Browse</strong> button, then activating it by clicking on <strong> Apply</strong>

<br></br>

On the right hand side of the screen is the parameter tab:

- <strong><ins>Neuron Parameters:</ins></strong>

  <p style='text-align: justify;'>
  Here users can manipulate most variables related to the neuron behaviour. These are a redundancy from the knobs on the spikeling device. When toggle buttons are enabled, the software take over the know and a digital value is displayed, allowing users an accurate and reliable settings of the spikeling neuron.

  - <ins>Injected Current:</ins>

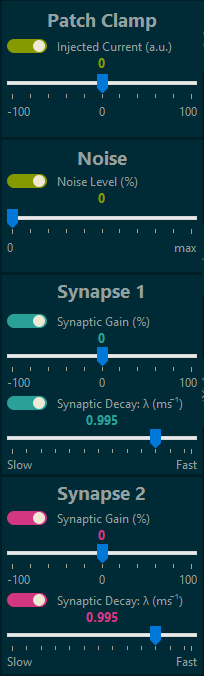
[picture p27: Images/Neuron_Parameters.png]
    

    <p style='text-align: justify;'>
    This parameter correspond to the amount of current (0 by default) injected into the neuron. It stimulates how an electrophysiology rig would perform a patch clamp experiment by holding the neuron current. Across the spikeling project, current are technically arbitrary units but can be explained to students as corresponding to mA.

    On the board, this corresponds to the bottom left knob

  - <ins>Noise:</ins>

    <p style='text-align: justify;'>
    No recording is noise free, unfortunately. This specific variable adds a random noise at different intensities in order to mimic noise from the environment, from the recording station, even the thermal noise from the neuronal tissue itself. This functions aims to educate students to appreciate how background noise affects recording and hides real spiking events. In advanced classes, this functions can be used to test the efficiency of a spike sorting algorithm.

    On the board, this corresponds to the bottom right knob

  - <ins>Synaptic Gain:</ins>

    <p style='text-align: justify;'>
    The synaptic gain corresponds to the polarity and strength of the synapse. Elicited spikes on the auxiliary spikeling devices trigger synaptic events on the main one. Such events can be enhanced, either positively (excitatory synapse) or negatively (inhibitory synapse). The resulting event is then integrated as an input current by the main spikeling device.

    <p style='text-align: justify;'>
    The strength of these synapses can be interpreted to students as the amount of vesicles released or even, the number of neurotransmitter receptors on the post synaptic membrane. The polarity of the synapse can be interpreted as the type of neurotransmitter released (i.e. Glutamate/GABA)

    On the board, these correspond to the knobs on the left

  - <ins> Synaptic Decay: </ins>

    <p style='text-align: justify;'>
    This variable is not present on the device and can only be manipulated on the GUI. It corresponds to the synapse dynamics, more explicitly, the rate at which a synaptic current will dissipate. It could be interpreted to students for example as the rate at which the neurotransmitter reuptake from the synaptic cleft occurs.

<br> </br>

- <strong><ins>Stimulus Parameters:</strong></ins>

  <p style='text-align: justify;'>
  This tab only concerns stimulation variables. On the spikeling device, the default stimulus consists of a square wave that is generated on the <strong>Stimulus Output</strong> plug at the bottom right of the board. Users on the board can modify the stimulus strength and frequency.

  <p style='text-align: justify;'>
  If the user want to directly stimulate the spikeling neuron (or an auxiliary unit connected via a synaptic input), a jack needs to be plugged from the <strong>Stimulus Output</strong> plug where it is generated, to the <strong> Current Input</strong> plug which can be interpreted to students as the experimental current applied to a neuron through a patching pipette during a classic electrophysiology experiment. Users can note that the diagram on top of the Spikeling board, represents such pipette.

  <p style='text-align: justify;'>
  Users can alternatively choose to plus the <strong>Stimulus Output</strong> plug to a jack-LED cord. The generated stimulus will then light up the LED which the user can then place on top of the represented <strong>Photoreceptor</strong> at the bottom of the board. It will be noted here that the light falls onto a photoreceptor outer segment, itself synapsing with the main neuron. The stimulation then becomes indirect via a photoactivation process.

  - <ins>Stimulus Frequency:</ins>

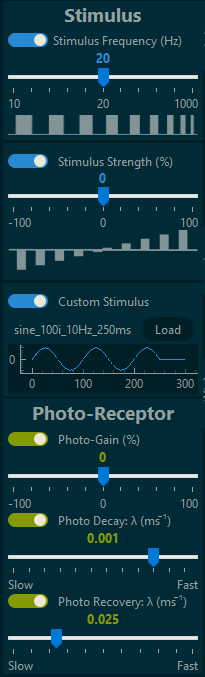
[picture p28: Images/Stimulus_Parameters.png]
    

    <p style='text-align: justify;'>
    As above, once a parameter is enabled, it takes over the value encoded by the know on the board.
    Here, this variable modulates the square wave stimulus frequency, from 10 to 1000Hz (related to the "Spikeling time", obviously slowed down here on the oscilloscope)

    On the board, it corresponds to the knob on the right, at the top

  - <ins>Stimulus Strength:</ins>

    <p style='text-align: justify;'>
    This variable is in arbitrary unit and corresponds to the strength and polarity of the square wave stimulus.

    On the board, it corresponds to the knob on the right, at the bottom.

  - <ins>Custom Stimulus:</ins>

    <p style='text-align: justify;'>
    Square wave stimuli are very handy to manipulate but can prove limited if not boring for advanced classes. Spikeling then comes with a stimulus generator (see below), where users can generate their own stimulation protocol.

    <p style='text-align: justify;'>
    Stimulus first need to be selected, by clicking on the <strong>Load</strong> button. A display of the stimulus will then appear on the little oscilloscope below. Stimulation will only be effective when the toggle button will be enabled.

  - <ins>Photo-Receptor - Photo-Gain:</strong>

    <p style='text-align: justify;'>
    This variable deals with the sensitivity and polarity of the photoreceptor. Units are arbitrary. It can be interpreted as variation amongst cell types, i.e. type of post-synaptic neurotransmitter receptors (ionotropic/metabotropic) to justify the polarity.

    On the board, it corresponds to the knob on the bottom, in the middle.

  - <ins>Photo-Receptor - Photo-Decay:</strong>

    <p style='text-align: justify;'>
    This variable is only accessible on the GUI and corresponds to the rate at which the photo current generated by the photoreceptor will dissipate.

  - <ins>Photo-Receptor - Photo-Recovery:</strong>

    <p style='text-align: justify;'>
    This variable is only accessible on the GUI and corresponds to the rate at which the current generated by the photoreceptor desaturates.

    By modulating the two variable above, users can modify the photoreceptor dynamics and generated different current input (i.e transient/sustained) that will in turn elicit different trains of spikes.

   <br></br>

   <p style='text-align: justify;'>
   Finally, the neuron interface comes with a recording system. Users needs to select a repository where to save their data, enter a file name (careful, similar filename will overwrite previous version).

   <p style='text-align: justify;'>
   Then by hitting the <strong>Record</strong> button, the current traces will be save in a .csv format.
   Recording will cease only when users would click on the <strong> Stop</strong> button.

<br></br>

<p style='text-align: justify;'>
Recorded data can be analysed on the go within the Spikeling tab menu, by selecting <strong>Data Analysis</strong>.
At the moment, only square wave data can be analysed here. Future updates will integrate more advanced data analysis. However jupyter-notebooks are available to analyse the data or users can just use the .csv file generated and analysed it on their programming language of choice. Currently a R version is being developed to be coupled with on going data analysis courses

<p style='text-align: justify;'>
First <strong>Load Data</strong> then follow the procedure. Only one variable is left here to the students, the threshold at which one can estimate a spike occurs. Different values might end up in quite different average traces.

At each step, users can displayed traces from other neurons if any were connected.

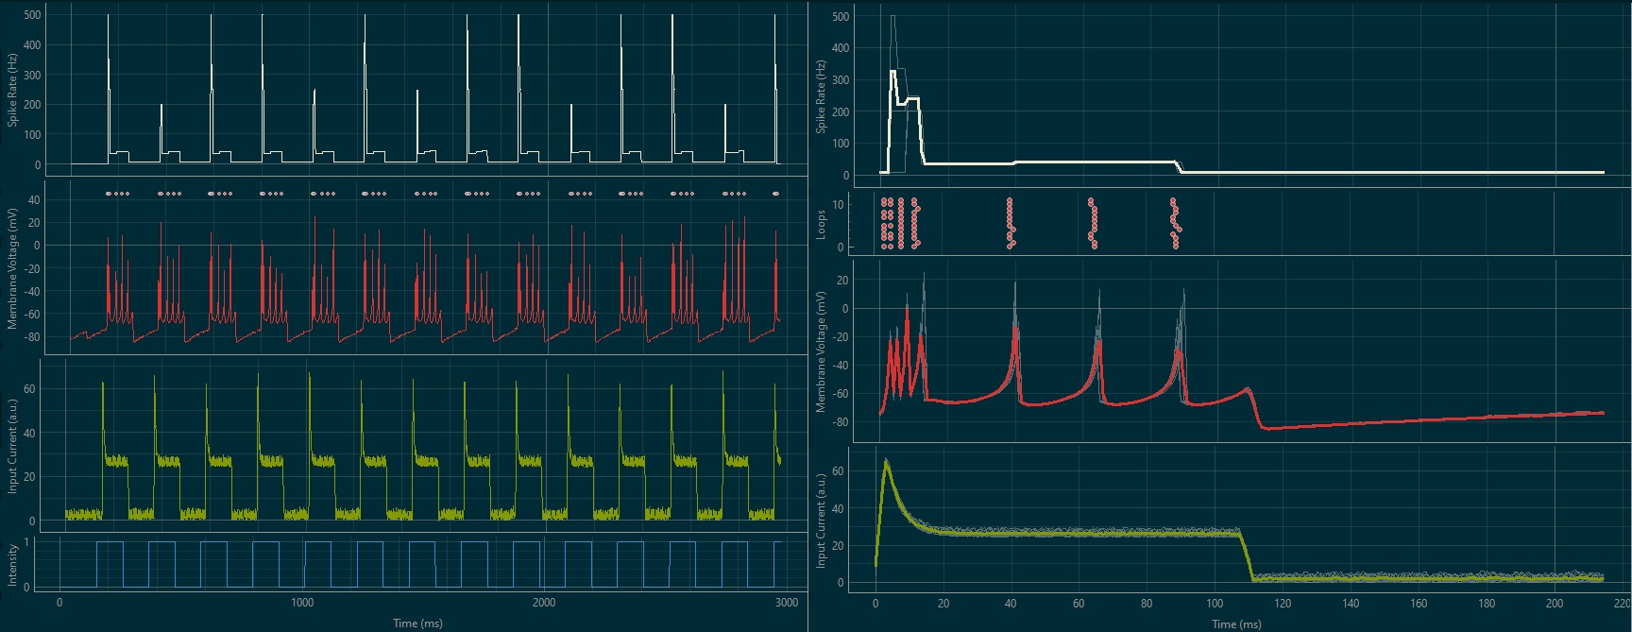
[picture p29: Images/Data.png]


<br></br>


<h4 align="left"> Imaging Menu</h4>

<p style='text-align: justify;'>
Spikeling receives many inputs but generates only one data, the neuron voltage membrane potential (Vm). Following diverse interactions, this Vm might cross a pre-defined threshold (-30mV) and elicit a spike. Since such spikes are identified and used by the device for various operations, they can also be used to feed a calcium model that would mimic the transient rise of calcium concentration within a neuron following a spike.
From then a second model could use such calcium transient trace to model a fluorescence trace as it could be observed under a two-photon microscope for example.

<p style='text-align: justify;'>
So let's now consider spikeling neuron as being a one pixel fluorescent object. By clicking on the <strong>Imaging Stimulation</strong> button, an oscilloscope displaying this one pixel fluorescence trace will pop up (Up tp three one pixel neuron fluorescence traces if users select the <strong> Multiple Imaging</strong> button).

<p style='text-align: justify;'>
By default, only the fluorescence trace is enabled, which is the data on which students should work on as it represents the data they will be faced with during a dynamic fluorescence recording experiment. But users can also display the Calcium trace that is used to generate the fluorescence one, as well as the Vm that we can consider here as the ground truth data.

On these sections, three parameter tabs can be explore, each considering a specific variable group:

- <strong><ins>Imaging Parameters</ins></strong>

  In this section, users can manipulate variable dependent of the experimental recording system itself.

  - <ins> Calcium Indicator:</ins>

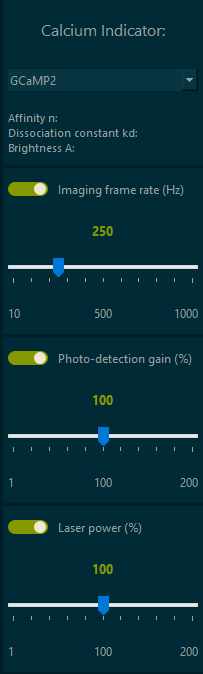
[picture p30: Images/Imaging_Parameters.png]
    

    <p style='text-align: justify;'>
    This section is a work in progress, but ultimately users could choose distinct calcium indicator models with different dynamics and kinetics properties. These are summed up in three variables (described on the calcium model equations): the indicator affinity to calcium, its dissociation constant and its brightness. These values are displayed on the parameter tab.

  - <ins> Imaging frame rate:</ins>

    <p style='text-align: justify;'>
    This variables correspond to the sampling rate for the fluorescence trace. The aim here is to let student appreciate, despite the fact that they are scanning a one pixel object, that they is an important trade off between the imaging rate and the necessity for a better scanning resolution. Point is that lower frame rate will miss some fluorescence event underlying spiking events.

  - <ins> Photo-detection gain:</strong>

    <p style='text-align: justify;'>
    This variable increases the fluorescence traces signal but incorporate some random noise as it goes into higher intensity. It can be interpreted as the PMT gain from a recording system.

  - <ins> Laser power:</ins>

    <p style='text-align: justify;'>
    This variable is similar to the previous one as it enhances the fluorescence signal, but integrates a decay counter that diminishes this effect overtime in a non reversible way, in order to simulate a photo-bleaching effect.

  <p style='text-align: justify;'>
  The two variables above must be manipulated together in order for students to appreciate the fine tuning of a recording setup in order to get a proper signal to noise ration while avoiding noise artefacts.

<br></br>

- <strong><ins>Calcium Parameters:</ins></strong>

  In this section users can manipulate calcium intrinsic properties of the neuron itself.

```math
[Ca^{2+}]_{t} = [Ca^{2+}]_{t-1} - \tau . [Ca^{2+}]_{t-1} + [Ca^{2+}]_{b} + A . n_{t} + \sigma_{Ca} . \sqrt{\Delta} . \varepsilon_{Ca,t}
```

  Where:
  - $\tau$ is the Calcium decay constant
  - $[Ca^{2+}]_{b}$ the Calcium baseline concentration
  - A is the calcium concentration jump each spike triggers
  - $n_{t}$ is the number of spikes at time t
  - $\sigma_{Ca}$ scales the Calcium noise
  - $\Delta$ represents the imaging frame timeline
  - $\varepsilon_{Ca,t}$ is a standard normal Gaussian noise source

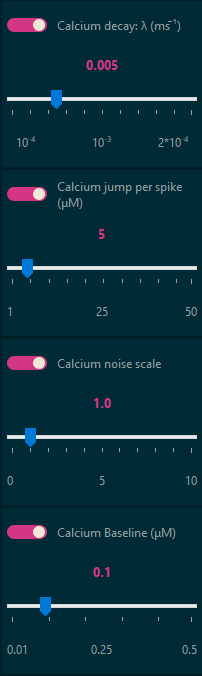
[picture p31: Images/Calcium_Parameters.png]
  

  - <ins>Calcium decay:</ins>

    <p style='text-align: justify;'>
    This corresponds to the rate at which a calcium event returns exponentially to its baseline concentration value with a time constant $\tau$ . This can be interpreted at the myriad of calcium extrusion and endogenous buffering mechanism and we sum it up into this single average time constant.

    $\tau  .  [Ca^{2+}]_{t-1}$

  - <ins>Calcium jump per spike:</ins>

    <p style='text-align: justify;'>
    This corresponds to the calcium concentration rise that follows each spike event. We assume here that each jump is of the same size. In this specific model we neglect the calcium concentration saturation effects due to channel inactivation and buffering (next model will consider them).

    $A . n_{t}$

  - <ins>Calcium noise scale:</ins>

    <p style='text-align: justify;'>
    Calcium concentration dynamics themselves have some Gaussian noise source, scaled by $\sigma_{Ca}$

    $\sigma_{Ca}$ . $\sqrt{\Delta}$ . $\varepsilon_{Ca,t}$

  - <ins> Calcium baseline:</ins>

    <p style='text-align: justify;'>
    This corresponds to the intrinsic intracellular concentration of calcium within the neuron at rest.

    $[Ca^{2+}]_{b}$

<br></br>
<br></br>

- <strong><ins>Fluorescence Parameters</ins></strong>

Finally this section deals with variables associated with the fluorescence itself.

```math
F_{t} = \alpha[Ca^{2+}]_{t} + \beta + \sigma_{F}.\varepsilon_{F,t}
 ```

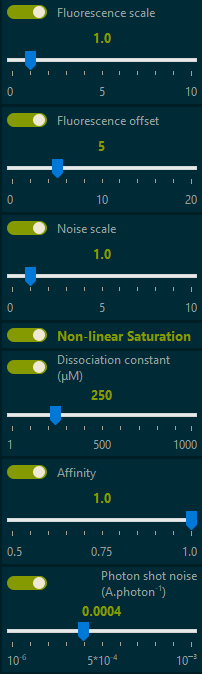
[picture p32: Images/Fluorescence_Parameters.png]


<p style='text-align: justify;'>
For this fluorescence model, we assume a single-compartmental, equipotential model of the imaged neuron, over which the fluorescence signal may be spatially averaged, yielding a one-dimensional time varying fluorescence signal for each image frame, $Ft$ (<a href="https://www.cell.com/fulltext/S0006-3495%2809%2900311-7">Vogelstein et al. 2009</a>).

Next, we assume that the fluorescence at any time is a noisy linear function of the calcium concentration at that time

 - The three first parameters, <strong>Fluorescence scale</strong>, <strong>Fluorescence offset</strong> and <strong>Noise scale</strong> respectively modulate the $\alpha$, $\beta$ and $\sigma$ terms of the above equation.

<br></br>

The relationship between the fluorescence signal and $[Ca2+]_{t}$ is often characterized by a nonlinear saturating function

```math
Fsat_{t} = \alpha.S.[Ca^{2+}]_{t} + \beta + \eta_{t}
```

This model can be activated by toggling the <strong>Non-linear Saturation</strong> button.

The fluorescence trace will then be quite more realistic and new variable are now available to modulate the fluorescence features.

  - <ins>Dissociation constant:</ins>

  <p style='text-align: justify;'>
  It represents $kd$ in the Hill equation: $S_{x} = x_{n} / (x_{n} + kd)$

  - <ins>Affinity:</ins>

  Represented by the Hill coefficient $n$ in the Hill equation above

  - <ins>Photon shot noise:</strong>

  <p style='text-align: justify;'>  
  The noise term, $\eta_{t}$ may be generalized similarly. Assuming the primary noise source is photon shot noise, it would be appropriate to model noise as a Poisson process, which could be well approximated by a Gaussian distribution for large photon counts:

  ```math
  \eta_{t} = \sqrt{\varepsilon.S . ([Ca^{2+}]_{t}) + \sigma_{F}} . \varepsilon_{F,t}
  ```

<br></br>

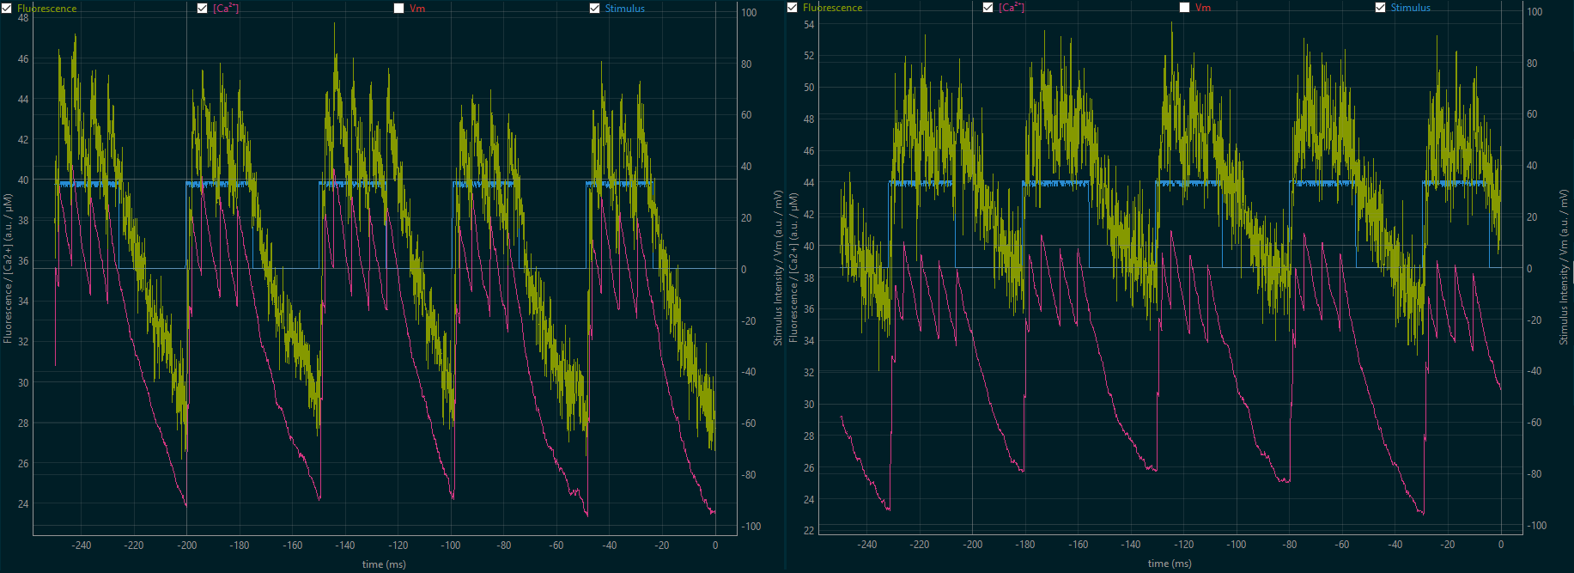
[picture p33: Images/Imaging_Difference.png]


<h6 align="center">Fluorescence imaging simulation differences between the linear model and the non-linear saturating model </h6>

<br></br>


<h4 align="left"> Neuron Generator Menu</h4>

<br></br>


<h4 align="left"> Stimulus Generator Menu</h4>

<br></br>


<h4 align="left"> Exercises Menu</h4>

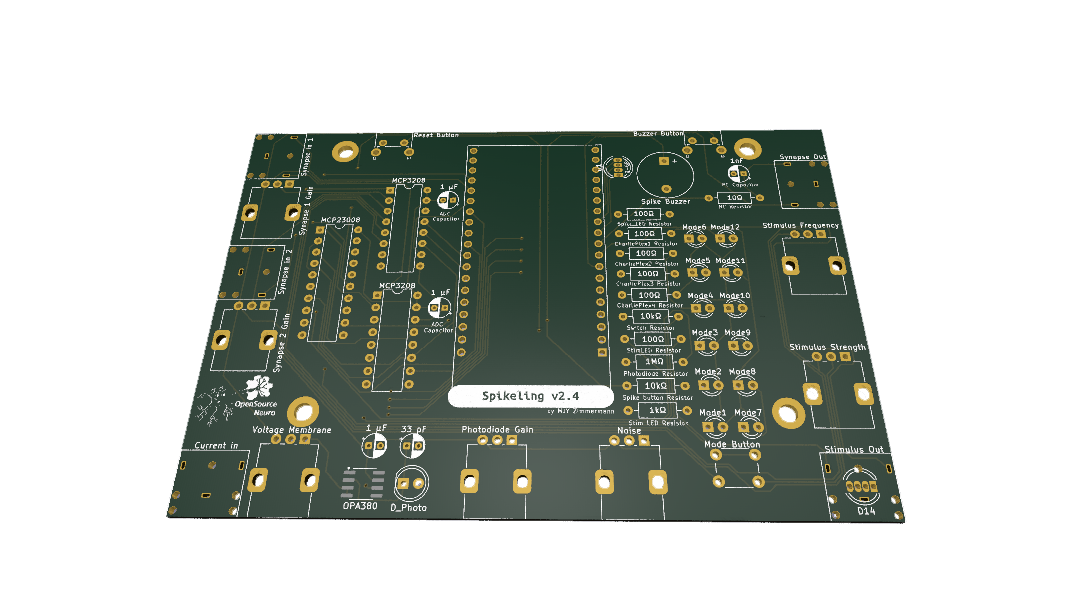
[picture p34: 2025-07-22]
Images/PrintedCircuitBoard_v2.4.png

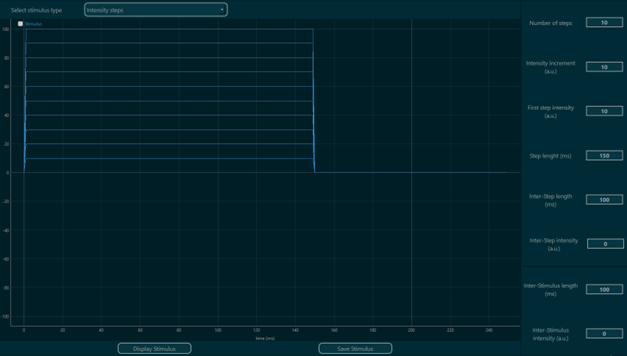
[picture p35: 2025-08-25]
GUI/PyQt/resources/InstensitySteps.png

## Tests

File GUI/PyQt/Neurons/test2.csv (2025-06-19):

a | b | c | d | PhotoGain (%) | PhotoDecay (1/ms) | PhotoRecovery (1/ms) | Syn1 Gain (%) | Syn1 Decay (1/ms) | Syn2 Gain (%) | Syn2 Decay (1/ms)
0.2 | 0.1 | -55 | 10 | 50 | 0.001 | 0.025 | 0 | 0.995 | 0 | 0.995

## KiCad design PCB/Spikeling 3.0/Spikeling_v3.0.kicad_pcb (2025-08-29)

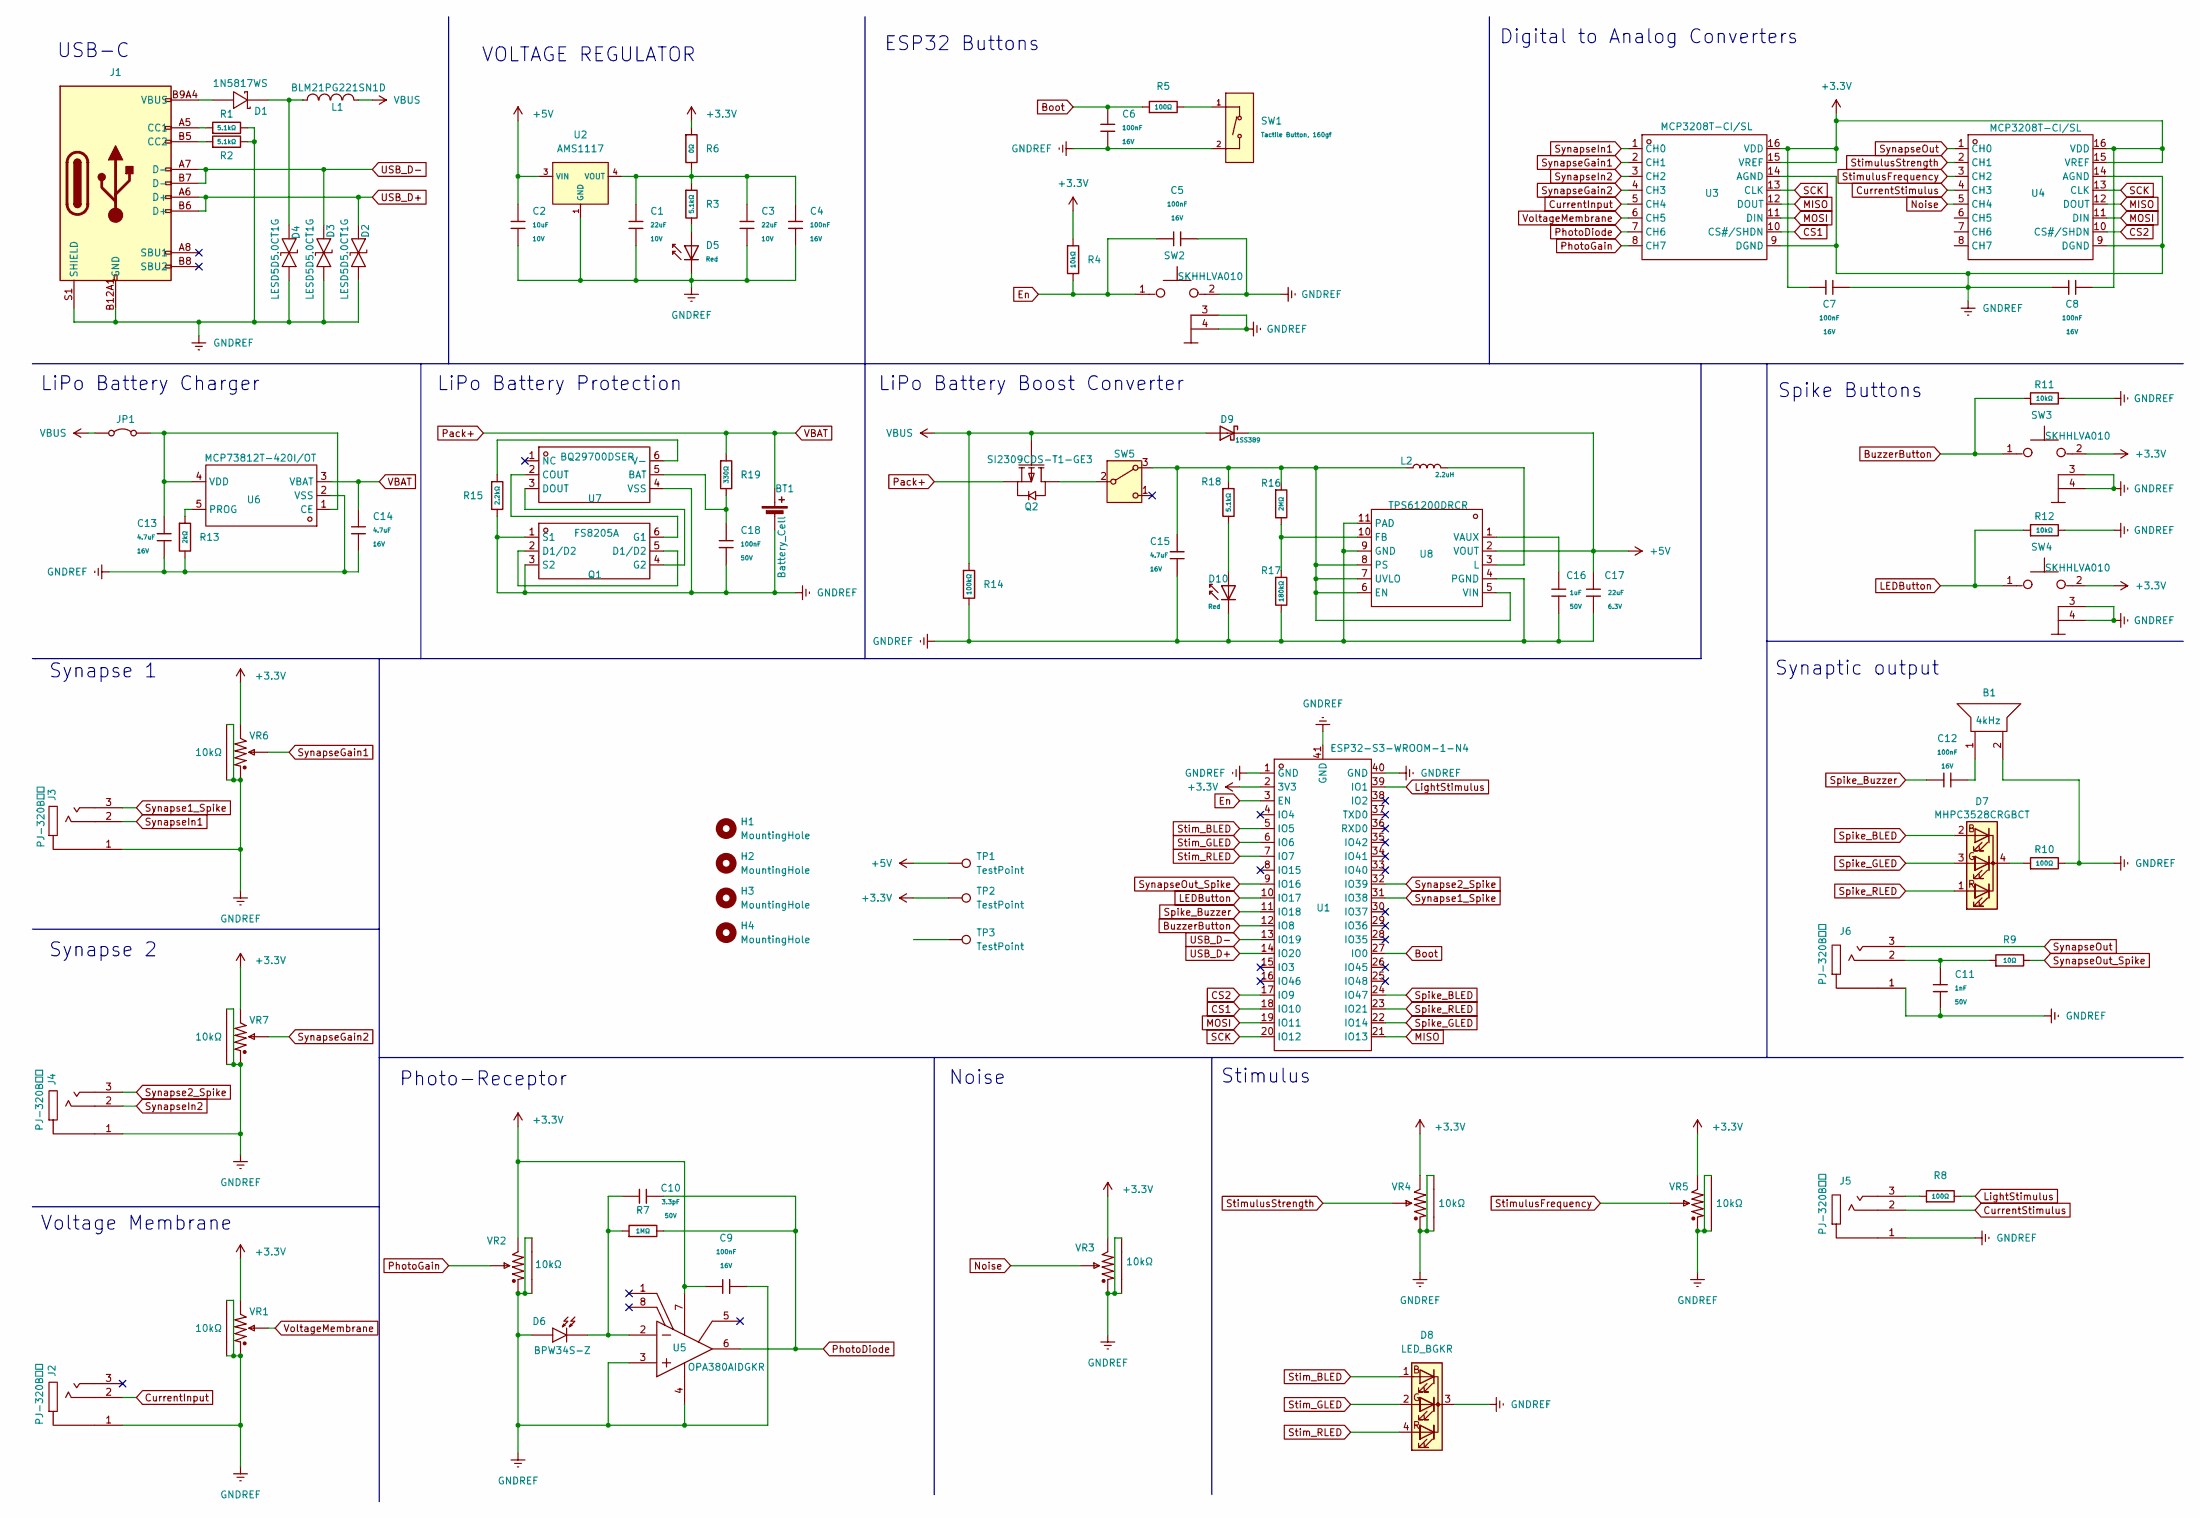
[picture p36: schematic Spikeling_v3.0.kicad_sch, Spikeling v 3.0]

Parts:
B1: 4kHz; BUZ-TH_L12.0-W12.0; VOLTAGE RATING 5V; MANUFACTURER PART KMTG1203; LCSC PART NAME KMTG1203 工业级-压电式无源贴片蜂鸣器
BT1: Battery_Cell; JST_XH_B2B-XH-A_1x02_P2.50mm_Vertical
C1, C3: 22uF; C_1206; Voltage Rated 10V; Tolerance ±10%; Part CL31A226KPHNNNE; LCSC C5672
C2: 10uF; C_0603; Voltage Rated 10V; Tolerance ±10%; Part CL10A106KP8NNNC; LCSC C19702
C4, C5, C6, C7, C8, C9, C12: 100nF; C_0402; Voltage Rated 16V; Tolerance ±10%; Part CL05B104KO5NNNC; LCSC C1525
C10: 3.3pF; C_0402; Voltage Rated 50V; Part 0402CG3R3C500NT; LCSC C1565
C11: 1nF; C_0603; Voltage Rated 50V; Tolerance ±10%; Part CL10B102KB8NNNC; LCSC C1588
C13, C14, C15: 4.7uF; C_0603; Voltage Rated 16V; Tolerance ±10%; Part CL10A475KO8NNNC; LCSC C19666
C16: 1uF; C_0603; Voltage Rated 50V; Tolerance ±10%; Part CL10A105KB8NNNC; LCSC C15849
C17: 22uF; C_0603; Voltage Rated 6.3V; Tolerance ±20%; Part CL10A226MQ8NRNC; LCSC C59461
C18: 100nF; C_0603; Voltage Rated 50V; Tolerance ±10%; Part CC0603KRX7R9BB104; LCSC C14663
D1: 1N5817WS; SOD-323_L1.8-W1.3-LS2.5-RD; FORWARD VOLTAGE (VF@IF) 750mV@3.1A; REVERSE VOLTAGE (VR) 20V; MANUFACTURER PART 1N5817WS; LCSC PART NAME 电压:20V 电流:1A
D2, D3, D4: LESD5D5.0CT1G; SOD-523_L1.2-W0.8-LS1.6-BI; CLAMPING VOLTAGE 18.6V; VOLTAGE - BREAKDOWN 5.6V; MANUFACTURER PART LESD5D5.0CT1G; LCSC PART NAME 双向ESD
D5, D10: Red; D_0603; Part KT-0603R; LCSC C2286
D6: BPW34S-Z; SENSOR-TH_BPW34S-Z; MANUFACTURER PART BPW34S-Z; LCSC PART NAME 920nm 频谱范围420nm~1120nm 反向电压32V
D7: MHPC3528CRGBCT; LED-SMD_4P-L3.2-W2.8-BL; LCSC PART NAME RGB三色 正贴
D8: LED_BGKR; LED_D5.0mm-4_RGB_Wide_Pins
D9: 1SS389; D_SOD-523; Part 1SS389; LCSC C22466369
H1, H2, H3, H4: MountingHole; MountingHole_3mm
J1: Connector, USB-TYPE-C-16P; TYPE-C-SMD_HX-TYPE-C-16PIN; LCSC C2927039
J2, J3, J4, J5, J6: PJ-320B贴片; AUDIO-SMD_PJ-320B; CURRENT RATING (MAX) 200mA; VOLTAGE RATING (MAX) 30V; MANUFACTURER PART PJ-320B贴片; LCSC PART NAME 3.5mm耳机座
JP1: Jumper; SolderJumper-2_P1.3mm_Open_Pad1.0x1.5mm
L1: BLM21PG221SN1D; L0805; TOLERANCE ±25%; CURRENT RATING 2A; MANUFACTURER PART BLM21PG221SN1D; LCSC PART NAME 单路 0805磁珠 阻抗220Ω@100MHz
L2: 2.2uH; L_0805; Tolerance ±10%; Part CMI201209U2R2KT; LCSC C1043
Q1: FS8205A; SOT-23-6; MANUFACTURER PART FS8205A; LCSC PART NAME 2个N沟道 耐压:20V 电流:6A
Q2: SI2309CDS-T1-GE3; SOT-23-3_L2.9-W1.3-P1.90-LS2.4-BR; MANUFACTURER PART SI2309CDS-T1-GE3; LCSC PART NAME 1个P沟道 耐压:60V 电流:1.6A
R1, R2, R3, R18: 5.1kΩ; R_0603; Overload Voltage (Max) 75V; Tolerance ±1%; Part 0603WAF5101T5E; LCSC C23186
R4, R11, R12: 10kΩ; R_0603; Overload Voltage (Max) 75V; Tolerance ±1%; Part 0603WAF1002T5E; LCSC C25804
R5, R8, R10: 100Ω; R_0603; Overload Voltage (Max) 75V; Tolerance ±1%; Part 0603WAF1000T5E; LCSC C22775
R6: 0Ω; R_0603; Overload Voltage (Max) 75V; Tolerance ±1%; Part 0603WAF0000T5E; LCSC C21189
R7: 1MΩ; R_0603; Overload Voltage (Max) 75V; Tolerance ±1%; Part 0603WAF1004T5E; LCSC C22935
R9: 10Ω; R_0603; Overload Voltage (Max) 75V; Tolerance ±1%; Part 0603WAF100JT5E; LCSC C22859
R13: 2kΩ; R_0603; Overload Voltage (Max) 75V; Tolerance ±1%; Part 0603WAF2001T5E; LCSC C22975
R14: 100kΩ; R_0603; Overload Voltage (Max) 75V; Tolerance ±1%; Part 0603WAF1003T5E; LCSC C25803
R15: 2.2kΩ; R_0603; Overload Voltage (Max) 75V; Tolerance ±1%; Part 0603WAF2201T5E; LCSC C4190
R16: 2MΩ; R_0603; Overload Voltage (Max) 75V; Tolerance ±1%; Part 0603WAF2004T5E; LCSC C22976
R17: 180kΩ; R_0603; Overload Voltage (Max) 75V; Tolerance ±1%; Part 0603WAF1803T5E; LCSC C22827
R19: 330Ω; R_0603; Overload Voltage (Max) 75V; Tolerance ±1%; Part 0603WAF3300T5E; LCSC C23138
SW1: Tactile Button, 160gf; SW_TS-1088-AR02016; Voltage Rating (Dc) 12V; Part TS-1088-AR02016; LCSC C720477
SW2, SW3, SW4: SKHHLVA010; KEY-TH_4P-L7.5-W6.8-P4.50-LS7.2; VOLTAGE RATING (DC) 12V; MANUFACTURER PART SKHHLVA010; LCSC PART NAME 6*6*5.85mm 卧插 轻触开关
SW5: SW_Nidec_CAS-120A1; SW-TH_MMP122-R
TP1, TP2, TP3: TestPoint; TestPoint_Pad_D2.0mm
U1: ESP32-S3-WROOM-1-N4; WIFIM-SMD_ESP32-S3-WROOM-1-N8; MANUFACTURER PART ESP32-S3-WROOM-1-N4; LCSC PART NAME 通用型Wi-Fi+低功耗蓝牙MCU模组
U2: AMS1117; SOT-223-3_L6.5-W3.4-P2.30-LS7.0-BR; Output Voltage 3.3V; Dropout Voltage 1.3V@(800mA); Part AMS1117-3.3; LCSC C6186
U3, U4: MCP3208T-CI/SL; SOIC-16_L9.9-W3.9-P1.27-LS6.0-BL; VOLTAGE - SUPPLY 2.7V~5.5V; MANUFACTURER PART MCP3208T-CI/SL; LCSC PART NAME MCP3208T-CI/SL
U5: OPA380AIDGKR; VSSOP-8_L3.0-W3.0-P0.65-LS4.9-BL; MANUFACTURER PART OPA380AIDGKR; LCSC PART NAME OPA380AIDGKR
U6: MCP73812T-420I/OT; SOT-23-5_L3.0-W1.7-P0.95-LS2.8-BR; VOLTAGE - SUPPLY 3.75V~6V; MANUFACTURER PART MCP73812T-420I/OT; LCSC PART NAME 单节锂离子/聚合物电池充电管理控制器
U7: BQ29700DSER; WSON-6_L1.5-W1.5-P0.50-TL; VOLTAGE - SUPPLY -300mV~8V; MANUFACTURER PART BQ29700DSER; LCSC PART NAME BQ29700DSER
U8: TPS61200DRCR; VSON-10_L3.0-W3.0-P0.50-TL-EP_TPS62410DRCR; VOLTAGE - SUPPLY 300mV~5.5V; OUTPUT VOLTAGE 1.8V~5.5V; MANUFACTURER PART TPS61200DRCR; LCSC PART NAME 低输入电压同步升压转换器
VR1, VR2, VR4, VR5, VR6, VR7: 10kΩ; RES-TH_RK09D1130C2P; TOLERANCE ±20%; VOLTAGE RATING 20V; MANUFACTURER PART RK09D1130C3C; LCSC PART NAME 10kΩ ±20%
VR3: 10kΩ; RES-TH_RK09D1130C2P; TOLERANCE ±20%; MANUFACTURER PART RK09D1130C2P; LCSC PART NAME 10kΩ ±20%

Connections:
+3.3V: C7.1, C8.2, C9.1, R4.1, R6.1, SW3.2, SW4.2, TP2.1, U1.2 (3V3), U3.15 (VREF), U3.16 (VDD), U4.15 (VREF), U4.16 (VDD), U5.7 (V+), VR1.3, VR2.3, VR3.3, VR4.3, VR5.3, VR6.3, VR7.3
+5V: C2.1, C17.1, D9.1, TP1.1, U2.3 (VIN), U8.2 (VOUT)
Boot: C6.1, R5.1, U1.27 (IO0)
BuzzerButton: R11.1, SW3.1, U1.12 (IO8)
CS1: U1.18 (IO10), U3.10 (CS#/SHDN)
CS2: U1.17 (IO9), U4.10 (CS#/SHDN)
CurrentInput: J2.2, U3.5 (CH4)
CurrentStimulus: J5.2, U4.4 (CH3)
En: C5.1, R4.2, SW2.1, U1.3 (EN)
LEDButton: R12.1, SW4.1, U1.10 (IO17)
LightStimulus: R8.2, U1.39 (IO1)
MISO: U1.21 (IO13), U3.12 (DOUT), U4.12 (DOUT)
MOSI: U1.19 (IO11), U3.11 (DIN), U4.11 (DIN)
unnamed: B1.1, C12.2
unnamed: C1.1, C3.1, C4.1, R3.1, R6.2, U2.2 (VOUT), U2.4 (VOUT)
unnamed: C11.1, J6.2, R9.1
unnamed: D1.1, D4.1, L1.1
unnamed: D1.2, J1.A9B4 (VBUS), J1.B9A4 (VBUS)
unnamed: D5.2, R3.2
unnamed: C10.2, D6.2 (C), R7.1, U5.2 (IN-)
unnamed: D7.4 (K), R10.1
unnamed: D10.2, R18.2
unnamed: J1.A5 (CC1), R1.1
unnamed: J1.B5 (CC2), R2.1
unnamed: J5.3, R8.1
unnamed 25: C13.1, JP1.2 (B), U6.1 (CE), U6.4 (VDD); also elsewhere on the board
unnamed: Q1.2 (D1/D2), Q1.5 (D1/D2)
unnamed: Q1.6 (G1), U7.2 (COUT)
unnamed: Q1.4 (G2), U7.3 (DOUT)
unnamed: Q2.3 (D), SW5.2 (B)
unnamed: R5.2, SW1.1 (A)
unnamed: R13.1, U6.5 (PROG)
unnamed: C18.1, R19.2, U7.5 (BAT)
unnamed: R16.2, R17.1, U8.10 (FB)
unnamed: L2.2, U8.3 (L)
unnamed: C16.1, U8.1 (VAUX)
Noise: U4.5 (CH4), VR3.2
Pack+: BT1.1 (+), C14.1, Q2.2 (S), R19.1, U6.3 (VBAT); also elsewhere on the board
PhotoDiode: C10.1, R7.2, U3.7 (CH6), U5.6 (OUT)
PhotoGain: U3.8 (CH7), VR2.2
SCK: U1.20 (IO12), U3.13 (CLK), U4.13 (CLK)
Spike_BLED: D7.2 (BA), U1.24 (IO47)
Spike_Buzzer: C12.1, U1.11 (IO18)
Spike_GLED: D7.3 (GA), U1.22 (IO14)
Spike_RLED: D7.1 (RA), U1.23 (IO21)
Stim_BLED: D8.1 (BA), U1.5 (IO5)
Stim_GLED: D8.2 (GA), U1.6 (IO6)
Stim_RLED: D8.4 (RA), U1.7 (IO7)
StimulusFrequency: U4.3 (CH2), VR5.2
StimulusStrength: U4.2 (CH1), VR4.2
Synapse1_Spike: J3.3, U1.31 (IO38)
Synapse2_Spike: J4.3, U1.32 (IO39)
SynapseGain1: U3.2 (CH1), VR6.2
SynapseGain2: U3.4 (CH3), VR7.2
SynapseIn1: J3.2, U3.1 (CH0)
SynapseIn2: J4.2, U3.3 (CH2)
SynapseOut: J6.3, U4.1 (CH0)
SynapseOut_Spike: R9.2, U1.9 (IO16)
USB_D+: D2.1, J1.A6 (D+), J1.B6 (D+), U1.14 (IO20)
USB_D-: D3.1, J1.A7 (D-), J1.B7 (D-), U1.13 (IO19)
VBUS: D9.2, JP1.1 (A), L1.2, Q2.1 (G), R14.1
VoltageMembrane: U3.6 (CH5), VR1.2

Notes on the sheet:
Spike Buttons
LiPo Battery Charger
Synapse 1
ESP32 Buttons
Synapse 2
LiPo Battery Boost Converter
Digital to Analog Converters
USB-C
Voltage Membrane
LiPo Battery Protection
Noise
Stimulus
VOLTAGE REGULATOR
Photo-Receptor
Synaptic output

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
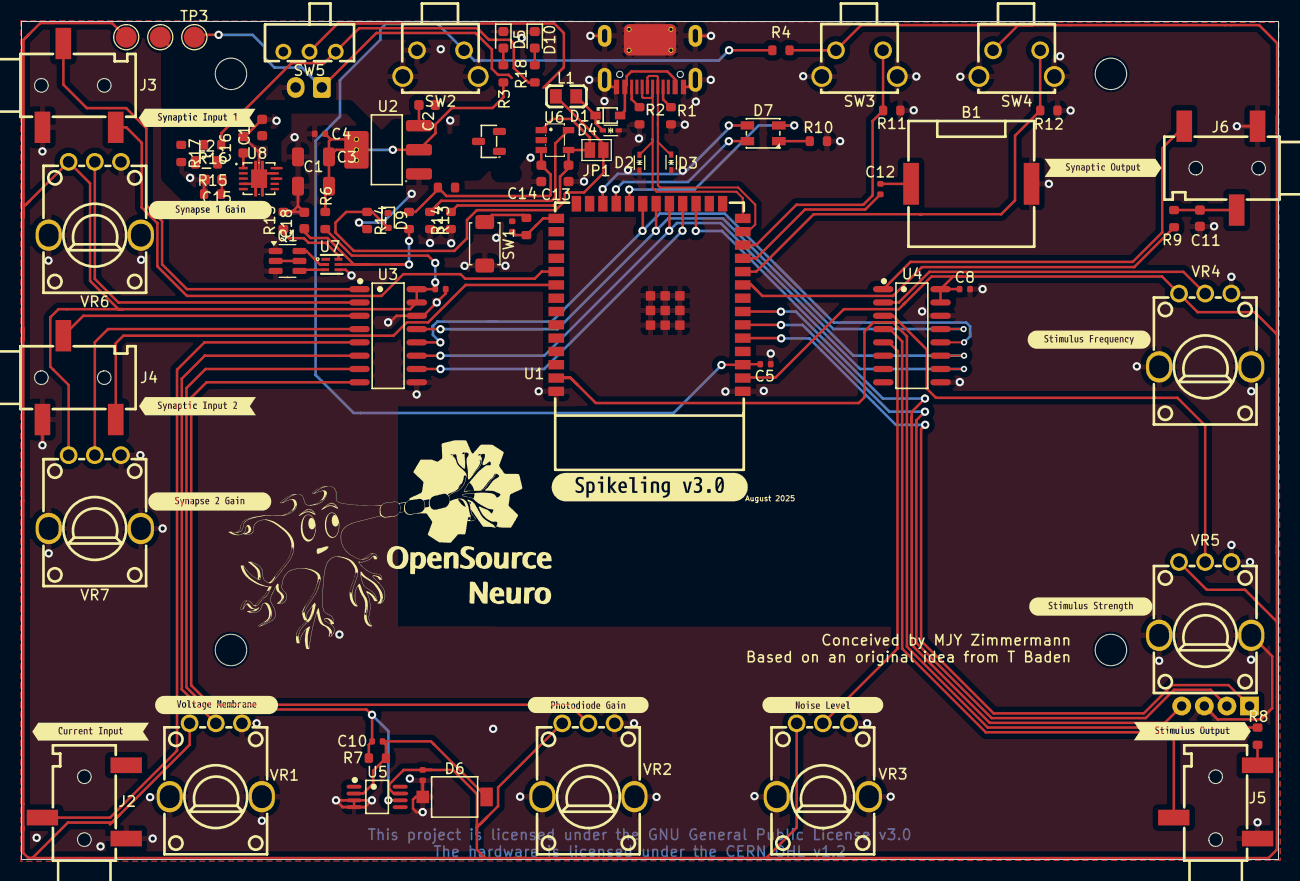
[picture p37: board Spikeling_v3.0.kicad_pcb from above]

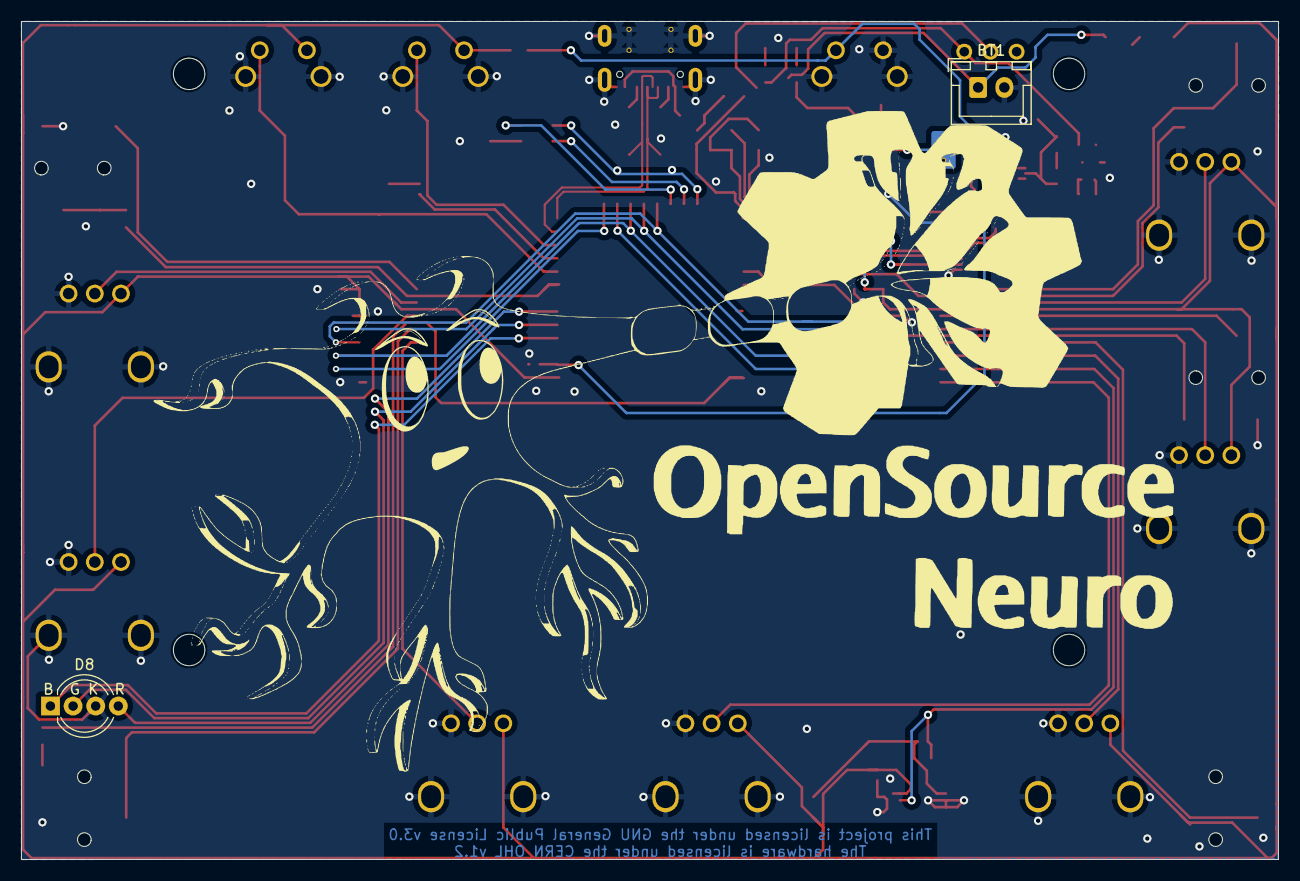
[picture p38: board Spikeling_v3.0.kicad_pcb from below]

Board: 2 copper layers, 120.0 x 80.0 mm, 105 parts (2 on the bottom side), 65 nets.

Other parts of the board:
.: Spikeling_neuron; Spikeling_Photoreceptor
.#2: Spikeling_neuron; Spikeling_Neuron
R14#2: 10kΩ; R_0603
R15#2: 2.2kΩ; R_0603
R21: 100kΩ; R_0603
kibuzzard-689381E8: G***; kibuzzard-689381E8
kibuzzard-689382F1: G***; kibuzzard-689382F1
kibuzzard-689383B5: G***; kibuzzard-689383B5
kibuzzard-689383D8: G***; kibuzzard-689383D8
kibuzzard-689384BB: G***; kibuzzard-689384BB
kibuzzard-6893830F: G***; kibuzzard-6893830F
kibuzzard-6893831F: G***; kibuzzard-6893831F
kibuzzard-6893832F: G***; kibuzzard-6893832F
kibuzzard-6893833B: G***; kibuzzard-6893833B
kibuzzard-68938301: G***; kibuzzard-68938301
kibuzzard-68938370: G***; kibuzzard-68938370
kibuzzard-68938494: G***; kibuzzard-68938494
kibuzzard-68972704: G***; kibuzzard-68972704

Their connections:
unnamed 25: R14#2.2; also elsewhere on the board
Pack+: R21.2; also elsewhere on the board

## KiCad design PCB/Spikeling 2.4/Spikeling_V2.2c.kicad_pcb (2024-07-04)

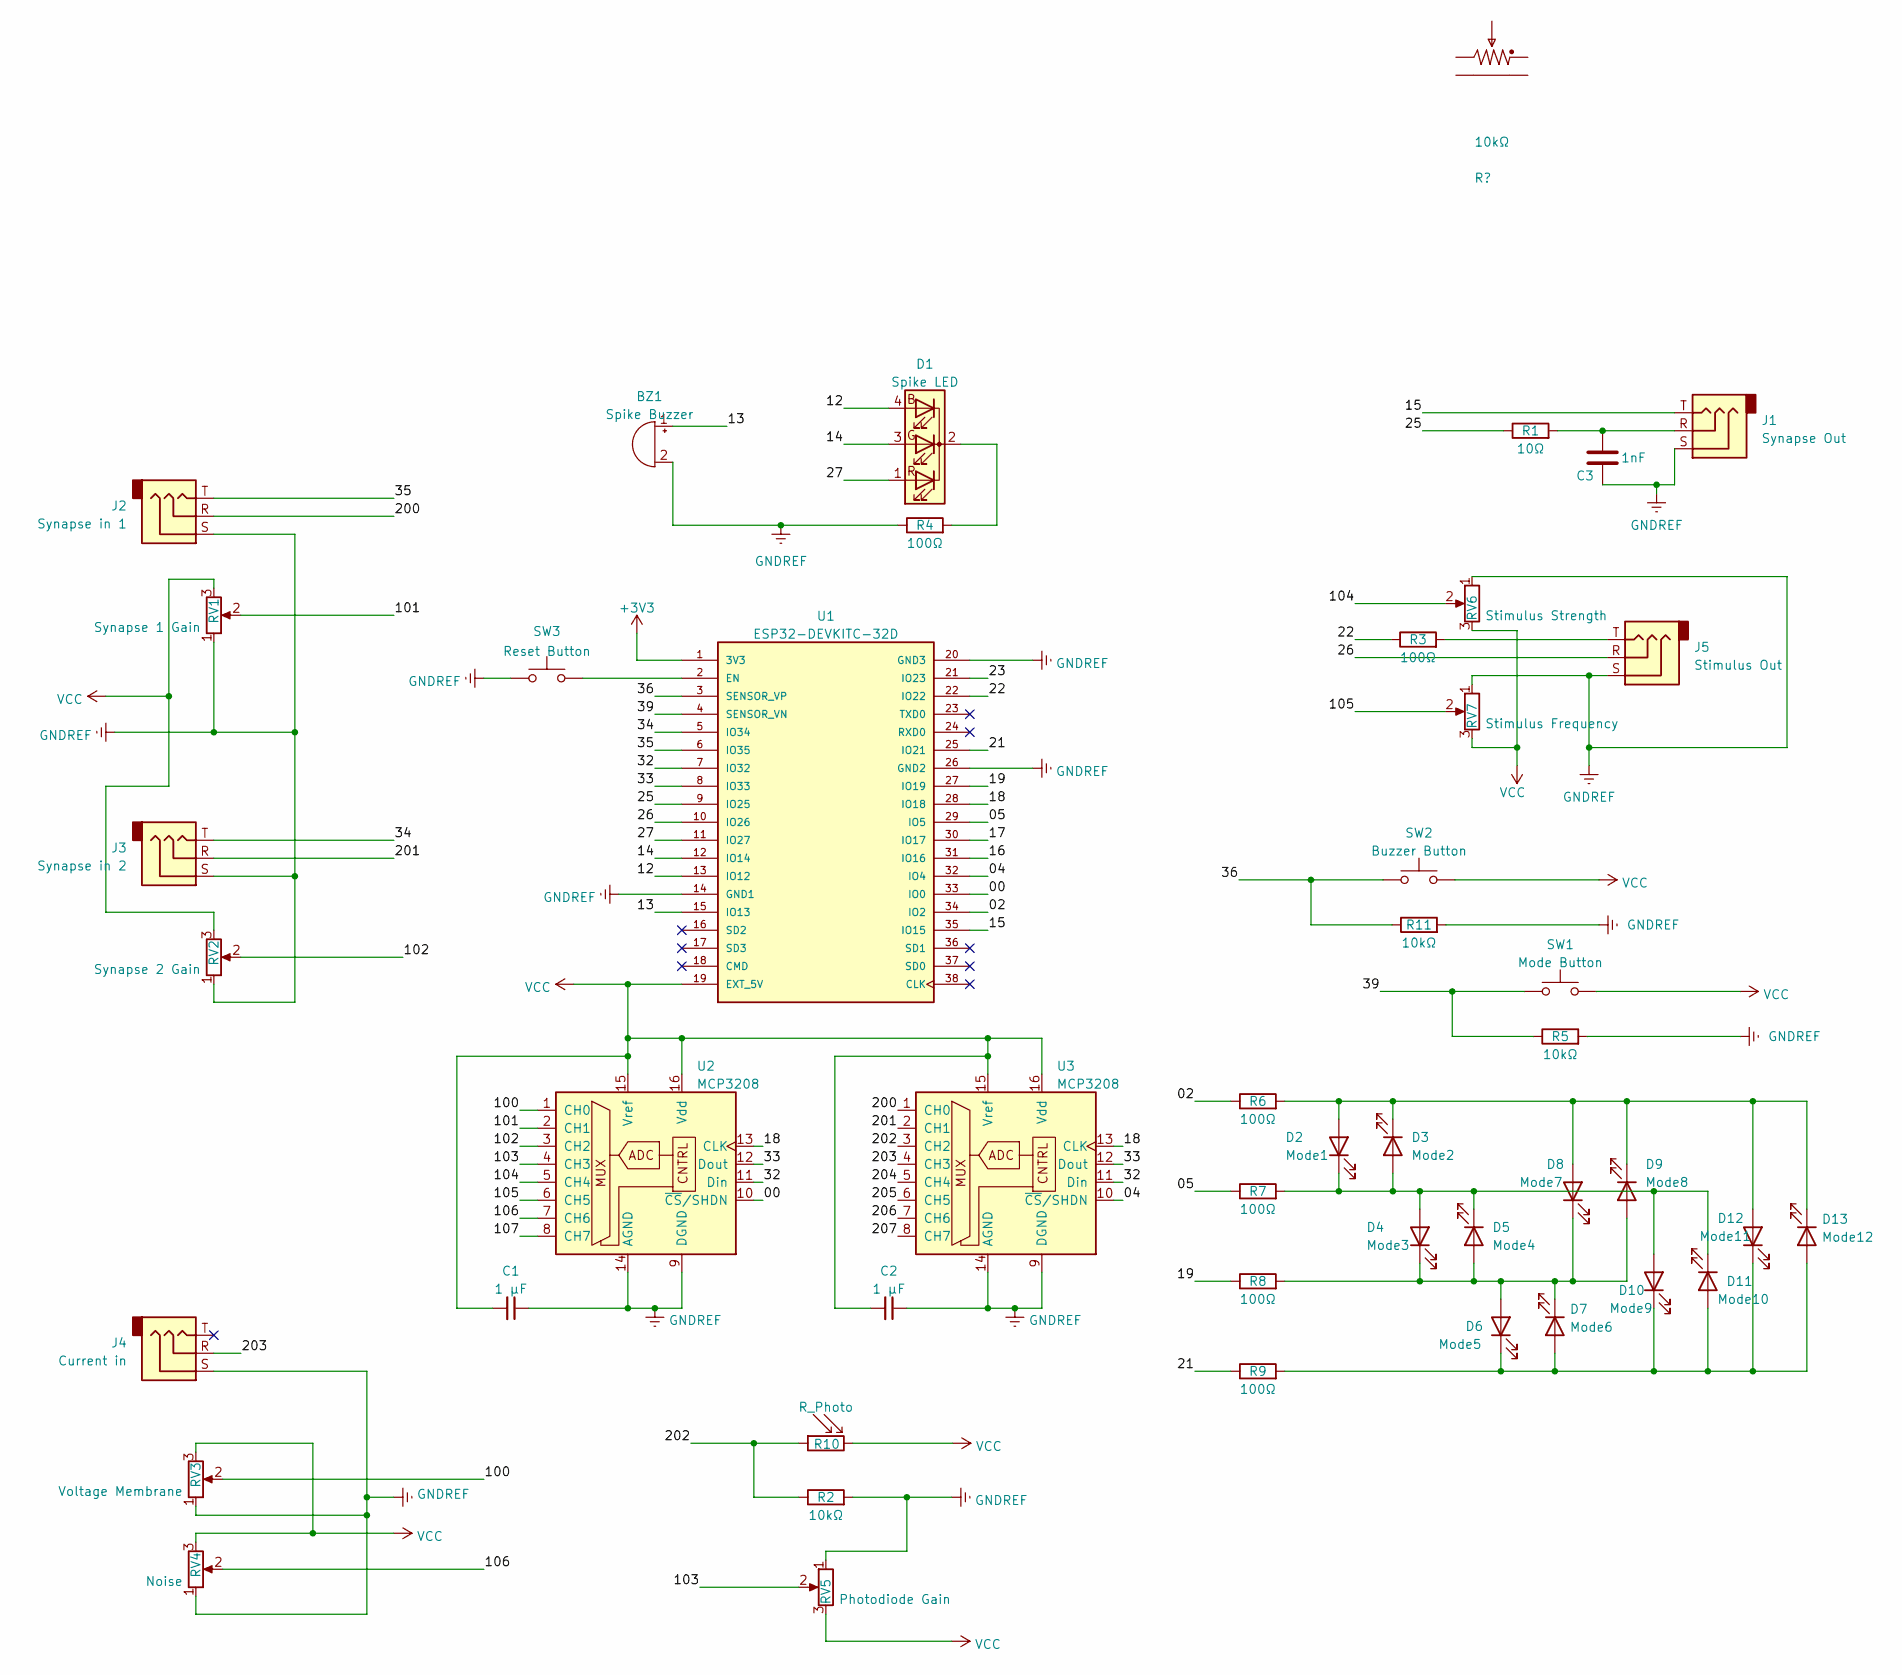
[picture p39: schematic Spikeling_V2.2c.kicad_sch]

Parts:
BZ1: Spike Buzzer; Buzzer_11.5x9.5RM5
C1, C2: 1 μF; CP_Radial_D4.0mm_P2.00mm
C3: 1nF; CP_Radial_D4.0mm_P2.00mm
D1: Spike LED; LED_D5.0mm-4_RGB
D2: Mode1; LED_D3.0mm
D3: Mode2; LED_D3.0mm
D4: Mode3; LED_D3.0mm
D5: Mode4; LED_D3.0mm
D6: Mode5; LED_D3.0mm
D7: Mode6; LED_D3.0mm
D8: Mode7; LED_D3.0mm
D9: Mode8; LED_D3.0mm
D10: Mode9; LED_D3.0mm
D11: Mode10; LED_D3.0mm
D12: Mode11; LED_D3.0mm
D13: Mode12; LED_D3.0mm
J1: Synapse Out; Spikeling Audio Jack 3.5mm
J2: Synapse in 1; Spikeling Audio Jack 3.5mm
J3: Synapse in 2; Spikeling Audio Jack 3.5mm
J4: Current in; Spikeling Audio Jack 3.5mm
J5: Stimulus Out; Spikeling Audio Jack 3.5mm
R1: 10Ω; R_Axial_DIN0207_L6.3mm_D2.5mm_P10.16mm_Horizontal
R2, R5, R11: 10kΩ; R_Axial_DIN0207_L6.3mm_D2.5mm_P10.16mm_Horizontal
R3, R4, R6, R7, R8, R9: 100Ω; R_Axial_DIN0207_L6.3mm_D2.5mm_P10.16mm_Horizontal
R10: R_Photo; Photoresistor_3.4
RV1: Synapse 1 Gain; Spikeling Potentiometer
RV2: Synapse 2 Gain; Spikeling Potentiometer
RV3: Voltage Membrane; Spikeling Potentiometer
RV4: Noise; Spikeling Potentiometer
RV5: Photodiode Gain; Spikeling Potentiometer
RV6: Stimulus Strength; Spikeling Potentiometer
RV7: Stimulus Frequency; Spikeling Potentiometer
SW1: Mode Button; SW_PUSH_6mm_H13mm
SW2: Buzzer Button; Spikeling reset button
SW3: Reset Button; Spikeling reset button
U1: ESP32-DEVKITC-32D; MODULE_ESP32-DEVKITC-32D; PARTREV 4
U2, U3: MCP3208; DIP-16_W7.62mm

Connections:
+3V3: U1.1 (3V3)
/00: U1.33 (IO0), U2.10 (~CS/SHDN)
/02: R6.1, U1.34 (IO2)
/04: U1.32 (IO4), U3.10 (~CS/SHDN)
/05: R7.1, U1.29 (IO5)
/12: D1.4 (BA), U1.13 (IO12)
/13: BZ1.1 (-), U1.15 (IO13)
/14: D1.3 (GA), U1.12 (IO14)
/15: J1.T, U1.35 (IO15)
/16: U1.31 (IO16)
/17: U1.30 (IO17)
/18: U1.28 (IO18), U2.13 (CLK), U3.13 (CLK)
/19: R8.1, U1.27 (IO19)
/21: R9.1, U1.25 (IO21)
/22: R3.1, U1.22 (IO22)
/23: U1.21 (IO23)
/25: R1.1, U1.9 (IO25)
/26: J5.R, U1.10 (IO26)
/32: U1.7 (IO32), U2.11 (Din), U3.11 (Din)
/33: U1.8 (IO33), U2.12 (Dout), U3.12 (Dout)
/34: J3.T, U1.5 (IO34)
/35: J2.T, U1.6 (IO35)
/36: R11.1, SW2.1, U1.3 (SENSOR_VP)
/39: R5.1, SW1.1, U1.4 (SENSOR_VN)
/100: RV3.2, U2.1 (CH0)
/101: RV1.2, U2.2 (CH1)
/102: RV2.2, U2.3 (CH2)
/103: RV5.2, U2.4 (CH3)
/104: RV6.2, U2.5 (CH4)
/105: RV7.2, U2.6 (CH5)
/106: RV4.2, U2.7 (CH6)
/107: U2.8 (CH7)
/200: J2.R, U3.1 (CH0)
/201: J3.R, U3.2 (CH1)
/202: R2.1, R10.1, U3.3 (CH2)
/203: J4.R, U3.4 (CH3)
/204: U3.5 (CH4)
/205: U3.6 (CH5)
/206: U3.7 (CH6)
/207: U3.8 (CH7)
GNDREF: BZ1.2 (+), C1.1, C2.1, C3.2, J1.S, J2.S, J3.S, J4.S, J5.S, R2.2, R4.1, R5.2, R11.2, RV1.1, RV2.1, RV3.1, RV4.1, RV5.1, RV6.1, RV7.1, SW3.1, U1.14 (GND1), U1.20 (GND3), U1.26 (GND2), U2.9 (DGND), U2.14 (AGND), U3.9 (DGND), U3.14 (AGND)
unnamed: C3.1, J1.R, R1.2
unnamed: D4.1 (K), D5.2 (A), D6.2 (A), D7.1 (K), D8.1 (K), D9.2 (A), R8.2
unnamed: D6.1 (K), D7.2 (A), D10.1 (K), D11.2 (A), D12.1 (K), D13.2 (A), R9.2
unnamed: D2.1 (K), D3.2 (A), D4.2 (A), D5.1 (K), D10.2 (A), D11.1 (K), R7.2
unnamed: D2.2 (A), D3.1 (K), D8.2 (A), D9.1 (K), D12.2 (A), D13.1 (K), R6.2
unnamed: J5.T, R3.2
unnamed: SW3.2, U1.2 (EN)
VCC: C1.2, C2.2, R10.2, RV1.3, RV2.3, RV3.3, RV4.3, RV5.3, RV6.3, RV7.3, SW1.2, SW2.2, U1.19 (EXT_5V), U2.15 (Vref), U2.16 (Vdd), U3.15 (Vref), U3.16 (Vdd)

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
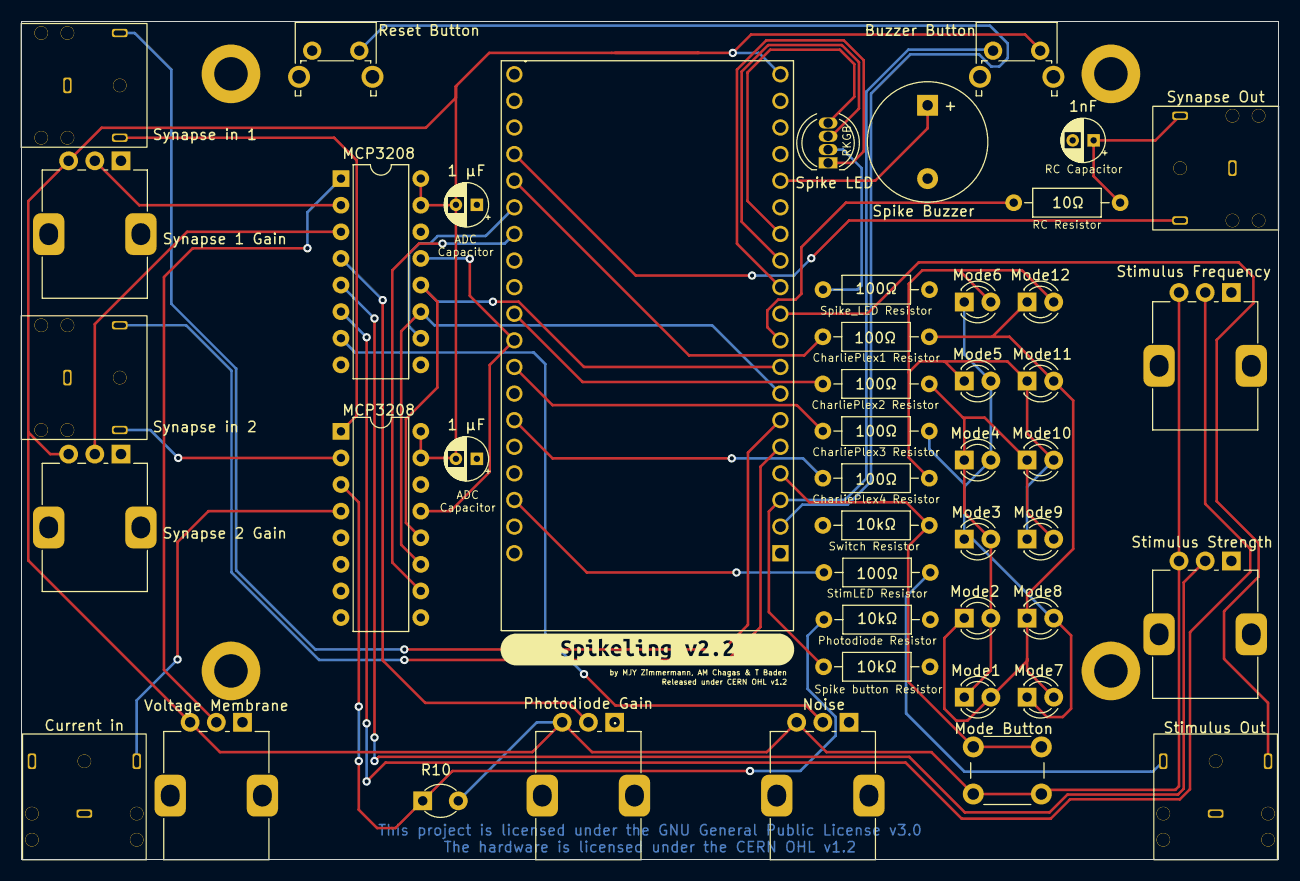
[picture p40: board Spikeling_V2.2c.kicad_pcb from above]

Board: 2 copper layers, 120.0 x 80.0 mm, 53 parts (0 on the bottom side), 42 nets.

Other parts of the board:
 : MountingHole_3.2mm_M3_DIN965_Pad
 #2: MountingHole_M3; MountingHole_3.2mm_M3_DIN965_Pad
 #3,  #4: MountingHole_3.2mm_M3_DIN965_Pad
.: Spikeling_neuron; Spikeling_Photoreceptor
.#2: Spikeling_neuron; Spikeling_Neuron
kibuzzard-633362FE: G***; kibuzzard-633362FE

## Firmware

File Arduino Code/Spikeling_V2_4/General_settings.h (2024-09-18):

/*          ---  General Settings  ---
*/

#include <MCP3208.h>
#include <KMP_MCP23S08.h>


// // // // // // // // // // // // // // // // // // // // // // // //
/*                       Hardware parameters                         */
int BaudRate = 250000;
int bits8 = 255;
int bits9 = 511;
int bits10 = 1023;
int bits11 = 2047;
int bits12 = 4095;
int bits = bits12;
int Mode = 0;
int ModeState = 0;

// // // // // // // // // // // // // // // // // // // // // // // //
/*                          Pin Definition                           */

int pin_CLK     =  18;
int pin_MOSI    =  23;
int pin_MISO    =  19;
int pin_CS1     =  0;
int pin_CS2     =  4;
int pin_CS3     =  5;
MCP3208 ADC1;
MCP3208 ADC2;
KMP_MCP23S08 DIO(pin_CS3);

int pinICPot       =   0;        // ADC 1.0: Inject Current potentiometer pin
int pinSpike       =   33;       // Buzzer pin

int pinSyn1_D      =   2;        // Input Digital pin for Synapse 1
int pinSyn1_A      =   0;        // ADC 2.0: Input Analog pin for Synapse 1
int pinSyn1Pot     =   1;        // ADC 1.1: Synapse 1 Gain potentiometer pin

int pinSyn2_D      =  15;        // Input Digital pin for Synapse 2
int pinSyn2_A      =   1;        // ADC 2.1:Input Analog pin for Synapse 2
int pinSyn2Pot     =   2;        // ADC 1.2: Synapse 2 Gain potentiometer pin
 
int pinAxon_D      =  3;        // Output Digital pin for the axon
int pinAxon_A      =  26;        // OutputAnalog pin for the axon

int pinPD          =   2;        // ADC 2.2:Photodiode reading pin
int pinPDPot       =   3;        // ADC 1.3: Photodiode Gain potentiometer pin

int pinModeButton  =   1;        // Mode Button pin
int pinBuzzer      =   0;        // Mute Buzzer pin
int pinStim_D      =   2;        // Output Digital pin for the stimulating LED
int pinStim_A      =  25;        // Output Analog pin for the stimulating Current Input pin
int pinStimStrPot  =   4;        // ADC 1.4: Stimulus amplitude potentiometer pin
int pinStimFrePot  =   5;        // ADC 1.5: Stimulus frequency potentiometer pin
int pinCurrentIn   =   3;        // ADC 2.3: Input Analog pin for CurrentIn stimuli
int pinNoisePot    =   6;        // ADC 1.6: Noise generator potentiometer pin
int pinLEDVm       =  27;
int pinLEDSpike1   =  14;
int pinLEDSpike2   =  12;


// // // // // // // // // // // // // // // // // // // // // // // //
/*                         Neuron parameters                         */
int      Vm_min    = -90;        // Minimum voltage value the v variable from Izhikevich can take
int      Vm_spike  = -30;        // Voltage value above which the neuron will spike
int      Vm_peak   =  30;        // Voltage peak value from which the v variable will start its recovery
boolean  spike     = false;      // Boolean used for registrating spike events
float    I_Total;                // Sum of all applied current to the neuron (I_IC, I_PD, I_Synapse1, I_Synapse2, I_Stim, I_Noise) 


// // // // // // // // // // // // // // // // // // // // // // // //
/*                     Voltage Clamp parameters                      */
int   IC_value;                  // Inject Current potentiometer value
int   IC_PotScaling =  bits/100;  // Inject Current value scaling - The lower, the stronger the impact of the IC potentiometer
float I_IC;                      // "Current" value generated from the two previous variables in order to modify the holding voltage value


// // // // // // // // // // // // // // // // // // // // // // // //
/*                       Synapse1 parameters                         */
int SpikeIn1State;               // Synapse 1 digital input
int Syn1_Gain;                   // Synapse 1 gain potentiometer value
float Syn1PotScaling =  bits/50;        // Synapse 1 gain sacaling - The lower, the stronger the impact of the Syn1_Potentiometer.  Default = 2
float Syn1_Amp;                    // Synapse 1 applied gain
int Syn1_offset = 100;
float I_Synapse1 = 0.0;                  // Synapse 1 input current
float Synapse1_decay = 0.995;      // Synpase 1 decay rate. The difference to 1 matters - the smaller the difference, the slower the decay. Default  = 0.995
int Syn1_Vm;

// // // // // // // // // // // // // // // // // // // // // // // //
/*                       Synapse2 parameters                         */
int SpikeIn2State;               // Synapse 2 digital input
int Syn2_Gain;                   // Synapse 2 gain potentiometer value
float Syn2PotScaling =  bits/50;        // Synapse 2 gain sacaling - The lower, the stronger the impact of the Syn2_Potentiometer.  Default = 2
float Syn2_Amp;                    // Synapse 2 applied gain
int Syn2_offset = 100;
float I_Synapse2 = 0.0;                  // Synapse 2 input current
float Synapse2_decay = 0.990;      // Synpase 2 decay rate. The difference to 1 matters - the smaller the difference, the slower the decay. Default  = 0.990
int Syn2_Vm;

// // // // // // // // // // // // // // // // // // // // // // // //
/*                         Axon parameters                           */
int Axon_AnalogOutput;
float Axon_AnalogScalling;
float Axon_AnalogInput1;
float Axon_AnalogInput2;
float Axon_AnalogOffset = -6.75;


// // // // // // // // // // // // // // // // // // // // // // // //
/*                      PhotoDiode parameters                        */
float PDPotScaling  = bits/25;    // the lower, the stronger the impact on PD_Gain
int   PD_PotRange = 10;
float PD_Gain=1.0;
float PD_PotValue;
float PD_Amp;
float PD_Value;
float PD_Scaling = 0.5;
int PD_Value_Array[] = {0,0,0,0,0,0,0,0,0,0};
int PD_counter = 0;
float PD_avg = 10;
float PD_Value_Sum;
float PD_Value_Average;
float PD_Decay = 0.001;
float PD_gain_mini = 0.0;  // the photodiode gain cannot decay below this value
float PD_Recovery = 0.025;
float I_PD;
int PD_Polarity = 1;


// // // // // // // // // // // // // // // // // // // // // // // //
/*                        Stimuli parameters                         */
int StimStr_Value;               // Stimulus Strength potentiometer value
int StimStrD;                     // Scaled stimulus strength
int StimStrA;
int StimStrA_mini = 10;
int Stim_minStr         = 2;     // Minimum stength value percentage below which the digital output is equal to 0
int Stim_val_D          = 0;     // Stimulus Digital output for stimulating LED
int Stim_val_A          = 0;     // Stimulus Analog output ofr Current in pin
int StimCus_val         = 0;
int StimCus_D           = 0;
int StimCus_A           = 0;
float Stim_state;                  // Status of the stimulus (ON or OFF / 1 or 0);
float StimLED_scaling     = 5.12;    // Scaling applied to the digital out value
int StimLED_offset = 10;
float Stim_CurrentScaling = 1.5;  // Scaling applied to the analog out value
float I_Stim_mini = 0.1;

int StimFre_Value;               // Stimulus Frequency potentiometer value
int StimFre;                     // Scaled stimulus frequency
int Stim_counter = 0;            // Stimulus step counter (number of void loops)
int Stim_steps = 0;              // Number of steps required for half a stimulus duty cycle
int Stim_DutyCycle = 500;        // Default stimulus duty cycle value
int Stim_minDutyCycle = 10;      // Minimum loop steps the stimulus duty cycle cannot fall under

int Stim_State;
int CurrentIn_Value;             // Stimulus Current-In value read for the voltage clamp
float CurrentInScaling = 0.1;
int I_Stim = 0;                  // Patch Current-In current


// // // // // // // // // // // // // // // // // // // // // // // //
/*                         Noise parameters                          */
int   Noise_Gain;                // Noise potentiometer value
int   NoiseScaling = 25;         // Noise gain scaling - The lower, the stronger the impact of the Noise_Potentiometer.  Default = 1000
int   Noise_Amp;                 // Noise applied gain
float I_Noise;                   // Noise current

// // // // // // // // // // // // // // // // // // // // // // // //
/*                         Rx Tx parameters                          */
boolean StimFre_Flag = true;  
boolean StimStr_Flag = true; 
boolean StimCus_Flag = true; 
boolean PDGain_Flag = true;
boolean PDDecay_Flag = true;
boolean PDRecovery_Flag = true;
boolean IC_Flag = true;
boolean Noise_Flag = true;
boolean Syn1Gain_Flag = true;
boolean Syn1Decay_Flag = true;
boolean Syn2Gain_Flag = true;
boolean Syn2Decay_Flag = true;
boolean Buzzer_Flag = true;
boolean LED_Flag = true;

String   OutputStr;

void HardwareSettings(){
  Serial.begin(BaudRate);

  ADC1.begin(pin_CLK, pin_MOSI, pin_MISO, pin_CS1);
  ADC2.begin(pin_CLK, pin_MOSI, pin_MISO, pin_CS2);
  DIO.begin();

  pinMode(pinSpike,OUTPUT);
  pinMode(pinLEDVm, OUTPUT);
  pinMode(pinLEDSpike1, OUTPUT);
  pinMode(pinLEDSpike2, OUTPUT);

  pinMode(pinSyn1_D,INPUT);
  pinMode(pinSyn2_D,INPUT);

  DIO.pinMode(pinAxon_D,OUTPUT);
  pinMode(pinAxon_A,OUTPUT);
  
  DIO.pinMode(pinModeButton,INPUT);
  DIO.pinMode(pinBuzzer,INPUT);
  
  DIO.pinMode(pinStim_D,OUTPUT);
  pinMode(pinStim_A,OUTPUT);

  digitalWrite(pinSpike,LOW);
  DIO.write(pinAxon_D,LOW);
  digitalWrite(pinAxon_A,LOW);
  DIO.write(pinStim_D,LOW);
  digitalWrite(pinStim_A,LOW);
  digitalWrite(pinLEDVm,LOW);
  digitalWrite(pinLEDSpike1,LOW);
  digitalWrite(pinLEDSpike2,LOW); 
}

float mapfloat(long x, long in_min, long in_max, long out_min, long out_max)
{
  return (float)(x - in_min) * (out_max - out_min) / (float)(in_max - in_min) + out_min;
}

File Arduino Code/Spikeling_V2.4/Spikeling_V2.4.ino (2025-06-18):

#include "Izhikevich_parameters.h"
#include "Serial_functions.h"


void setup() {
  HardwareSettings();
  Izhikevich_opening();
  SerialFunctions();
  SerialBlank();
  Mode_opening(); 
}


void loop() {
  
  SCmd.readSerial();

// // // // // // // // // // // // // // // // // // // // // // // // // // // // // // // // // // // // 
/*                                     Define Spikeling Mode                                             */
  ModeState = digitalRead(pinModeButton);         // Read the mode button state
  if (ModeState == HIGH){                         // If the mode button is pushed:
    Mode += 1;                                      // Increment the Mode by 1
    lightOn(Mode);                                  // Turn next Mode_LED
    a_Izhikevich = Array_a_Izhikevich[Mode];        // Change Izhikevich parameter a to the new mode
    b_Izhikevich = Array_b_Izhikevich[Mode];        // Change Izhikevich parameter b to the new mode
    c_Izhikevich = Array_c_Izhikevich[Mode];        // Change Izhikevich parameter c to the new mode
    d_Izhikevich = Array_d_Izhikevich[Mode];        // Change Izhikevich parameter d to the new mode

    if (Mode >= nModes){                          // If Mode has reached the maximum number of existing modes:
      Mode = 0;                                     // Reset Mode to 0
      lightOn(Mode);                                // Turn First Mode_LED
      a_Izhikevich = Array_a_Izhikevich[Mode];      // Change Izhikevich parameter a to the first mode
      b_Izhikevich = Array_b_Izhikevich[Mode];      // Change Izhikevich parameter b to the first mode
      c_Izhikevich = Array_c_Izhikevich[Mode];      // Change Izhikevich parameter c to the first mode
      d_Izhikevich = Array_d_Izhikevich[Mode];      // Change Izhikevich parameter d to the first mode
    }
    
    delay(Mode_delay);                            // Set a delay to prevent multi_push from the user
  }


// // // // // // // // // // // // // // // // // // // // // // // // // // // // // // // // // // // // 
/*                               Setting Voltage membrane clamp value                                    */

  if (IC_Flag == true){
    IC_value = ADC1.readADC(pinICPot) - bits/2;       // Reads IC potentiometer value and scales it to -2048 to 2048

    if (-IC_PotOffset < IC_value <= IC_PotOffset){
      I_IC = 0;
    }

    if (IC_value >= IC_PotOffset){
      I_IC = (IC_value - IC_PotOffset) / IC_PotScaling ;                 // Generates "current" value from the reading and scales it from parameters
    }
    if (IC_value <= -IC_PotOffset){
      I_IC = (IC_value + IC_PotOffset) / IC_PotScaling;                 // Generates "current" value from the reading and scales it from parameters
    }
  }
  


// // // // // // // // // // // // // // // // // // // // // // // // // // // // // // // // // // // // 
/*                                          Noise Generator                                              */

  Noise_Gain = ADC1.readADC(pinNoisePot);           // Reads Noise potentiometer value from 0 to 4095
  if (Noise_Flag == true){
    if (Noise_Gain <= Noise_PotOffset){
      I_Noise = 0;
    }
    else {
      Noise_Amp = (Noise_Gain - Noise_PotOffset) / NoiseScaling;          // Generates current value from the reading and scales it from parameters
      Gaussian Noisy (0,Noise_Amp/2);
      I_Noise = Noisy.random();
    }
  }

  if (Noise_Flag == false){
    I_Noise = I_Noise_Gen;
  }



// // // // // // // // // // // // // // // // // // // // // // // // // // // // // // // // // // // // 
/*              Reading PhotoDiode value and setting PhotoDiode gain for generating input current        */
  PD_Value = ADC2.readADC(pinPD);                   // Reads Photodiode value from 0 to ~400
  
  if ( PD_counter < PD_avg ){                     // If, for this void loop, the PD counter has not reached the max count number:
    PD_counter +=1;                                 // Increment the counter by 1
  }
  else{                                           // If the PD counter has reached the max count number:
    PD_counter = 0;                                 // Reset the counter to 0
  }
  PD_Value_Array[PD_counter] = PD_Value;          // For this void loop, assign the current PD value to the PD_Value_Array at the current counter position
  PD_Value_Sum = 0;                               // Reset the previous PD_Value_Sum
  for ( int i = 0; i < PD_avg; i++){              // For all current PD_array values:
    PD_Value_Sum += PD_Value_Array[i];              // Sum up all values within the array...
  }
  PD_Value_Average = PD_Value_Sum / PD_avg;       // ... then average them

  if (PDGain_Flag == true){
    PD_PotValue = ADC1.readADC(pinPDPot) - bits/2; // Reads Photodiode Gain potentiometer value and scales it to -2048 to 2048
    PD_Amp = map(PD_PotValue, -bits/2, bits/2, -PD_PotRange, PD_PotRange)+0.5;
  }

  if (PD_Amp >= 0){
    PD_Polarity = 1;
  }
  if (PD_Amp < 0){
    PD_Polarity = -1;
  }
  
                   // Generates an amplification value from the reading and scales it from parameters 

  I_PD = (PD_Value_Average * PD_Amp / PD_Scaling) * PD_Gain;  // Finally, generates a current input from the photodiode readings, amplified byt the PD_Gain readings

  if (PDDecay_Flag == true){
    PD_Decay = 0.001;
  }
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

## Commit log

2023-03-10 First upload
    [1-click-bom.csv, AuxNeuron1_means.csv, AuxNeuron1_rasterplot.csv, AuxNeuron2_means.csv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]
2023-03-15 upload windows version
    [AuxNeuron1_means.csv, AuxNeuron1_rasterplot.csv, AuxNeuron2_means.csv, AuxNeuron2_rasterplot.csv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]
2023-03-17 update arduino code - fix negative photo gain increment
2023-03-21 update Arduino code
2023-03-21 Upload custom stimuli examples
    [sine_100i_10Hz_250ms.csv, sine_50i_20Hz_200ms.csv, steps_10x10_50ms.csv, steps_10x5_25ms.csv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]
2023-04-10 update data examples
    [1Synapse_DC.csv, Synapse12_DC.csv]
2023-04-25 Update Arduino
2023-07-05 update stimuli
    [steps_10x10_20ms.csv, steps_10x10_30ms.csv, steps_20x5_20ms.csv]
2023-07-05 update PCB
    [1-click-bom.csv, Spikeling_V2.2b.csv, Spikeling_V2.2c-B_Courtyard.gbr, Spikeling_V2.2c-B_Cu.gbr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]
2025-06-19 update PyQt
    [.csv, 1Synapse_DC.csv, AuxNeuron1_means.csv, AuxNeuron1_rasterplot.csv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]
2025-06-19 update repository structure
    [AuxNeuron1_means.csv, AuxNeuron1_rasterplot.csv, AuxNeuron2_means.csv, AuxNeuron2_rasterplot.csv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]
2025-06-29 update neurons
    [TonicBursting_LightOffSustained.csv, TonicBursting_LightOffTransient.csv, TonicBursting_LightOnSustained.csv, TonicBursting_LightOnTransient.csv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]
2025-06-29 update recordings
    [gtyg .csv, szdxfgfdzx .csv, test .csv, testest .csv]
2025-06-29 update windows repo
    [TonicBursting_LightOffSustained.csv, TonicBursting_LightOffTransient.csv, TonicBursting_LightOnSustained.csv, TonicBursting_LightOnTransient.csv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]
2025-06-30 update linux
    [TonicBursting_LightOffSustained.csv, TonicBursting_LightOffTransient.csv, TonicBursting_LightOnSustained.csv, TonicBursting_LightOnTransient.csv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]
2025-06-30 update mac
    [TonicBursting_LightOffSustained.csv, TonicBursting_LightOffTransient.csv, TonicBursting_LightOnSustained.csv, TonicBursting_LightOnTransient.csv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]
2025-08-28 clean platform repositories
    [TonicBursting_LightOffSustained.csv, TonicBursting_LightOffTransient.csv, TonicBursting_LightOnSustained.csv, TonicBursting_LightOnTransient.csv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]

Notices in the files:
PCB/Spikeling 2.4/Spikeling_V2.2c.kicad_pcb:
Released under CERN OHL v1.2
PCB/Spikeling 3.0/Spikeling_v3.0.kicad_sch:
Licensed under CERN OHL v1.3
